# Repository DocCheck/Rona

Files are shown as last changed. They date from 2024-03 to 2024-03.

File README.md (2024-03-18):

# Rona - the Robotic Nurse Assistant

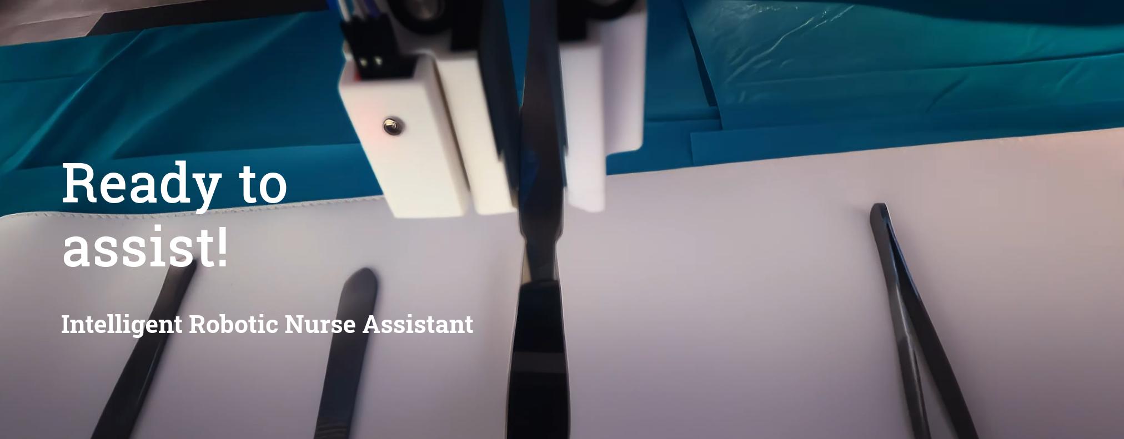
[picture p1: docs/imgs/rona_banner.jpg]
(https://more.doccheck.com/en/rona/)


# Meet Rona - your Open Source assistant for surgical procedures

Rona is an upgrade kit for robotic arms designed to address the problem with declining numbers of nurses in hospitals in
Germany, but also around the world. Rona's development is dedicated to create an affordable, easy to use, one-of-a-kind
software upgrade for surgery procedures and interventions where an additional hand is required, but a human support
might not be available.

The idea is to build an add-on that can be modular enough to be applicable to different robotic arms.
The system can be used with customizable machine learning models for instrument detection, angle estimation and wake-word detection.

For more information visit also: https://more.doccheck.com/en/rona/ 

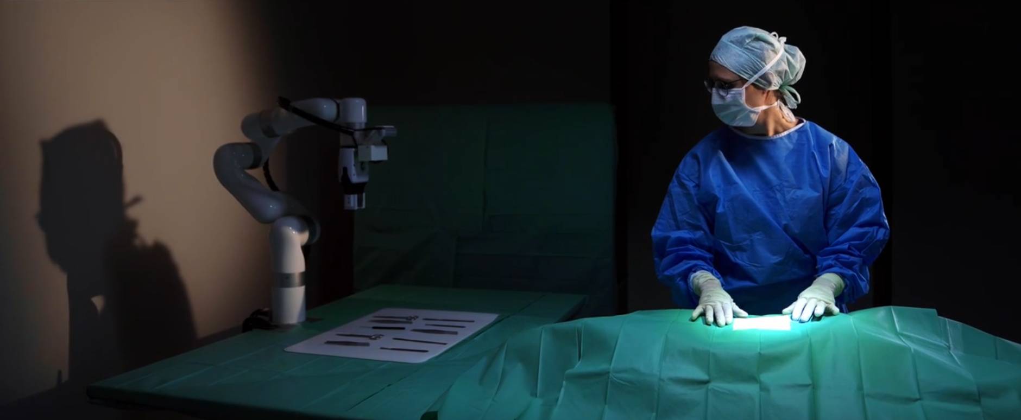
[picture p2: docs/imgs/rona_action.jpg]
Rona in Action (https://more.doccheck.com/en/rona/)


# Project Overview

## Requirements

### Hardware

Required hardware:

- a robotic arm. Currently only the [UFactory xArm5](https://www.ufactory.cc/xarm-collaborative-robot/) is supported
- a two-finger gripper e.g. [UFactory xArm Gripper](https://www.ufactory.cc/product-page/ufactory-xarm-gripper/) for the
  xArm5
- a camera holder for the robot e.g. [UFactory camera stand](https://www.ufactory.cc/product-page/ufactory-xarm-camera-stand/)
- a depth camera. Currently only the [Intel Realsense D435](https://www.ufactory.cc/xarm-collaborative-robot/) is  supported and tested in this setup
- a suitable microphone 
- a RaspberryPi Pico
- a [SW420 vibration sensor](https://www.az-delivery.de/en/products/sw420-vibration-schuttel-erschutterung-sensor-modul)
- 3D printable gripper tips, mounts and casings. CAD files can be found in the [3D models](docs/parts) folder
- cables and screws (more details in the assembly tutorial below)

For assembly and setup of the hardware parts check the [assembly tutorial](docs/assembly_tutorial.md) first.

### Software

Required software:

- [Linux machine with Ubuntu 22.04](https://ubuntu.com/download/desktop)
- [ROS2 Humble](https://docs.ros.org/en/humble/Installation.html)
- [Python 3.10+](https://www.python.org/downloads/)
- [Intel® RealSense™ SDK 2.0](https://github.com/IntelRealSense/librealsense/blob/master/doc/distribution_linux.md)
- [UFactory xArm-Python-SDK Version 1.13.0](https://github.com/xArm-Developer/xArm-Python-SDK) 
- various libraries python libraries explained in the [quickstart guide](docs/quickstart.md)

To install the software and the necessary libraries follow the [quickstart guide](docs/quickstart.md) \
For more detailed information on each ROS2 module check the [module documentation](docs/modules.md).

## Installation
- Get the necessary hardware listed in the [assembly guide](docs/assembly_tutorial.md) and follow it for the full assembly of the system.
- Follow the [quickstart guide](docs/quickstart.md) and install the necessary software, train or download all the necessary models for instrument detection, angle estimation and wake-word detection. 
- Do the [one-time configurations](docs/config.md) before you can continue with the usage of Rona

# How to use Rona
## Starting the system
Make sure you followed the [assembly guide](docs/assembly_tutorial.md), the [quickstart guide](docs/quickstart.md) and the [configuration](docs/config.md) before proceeding.
If everything is done successfully, you can start with the following commands in the rona_ws/ folder:

```bash
# Build and source the packages again just in case
$ make build-workspace

# Start system
$ make start-system
```

When Rona successfully boots up she will inform the user vocally that she is ready. 

## Wake word
In idle mode Rona will listen for her wake-word "Hey, Rona...". If she hears it she will open her gripper to signal that she starts listening for commands. 

          User: "Hey, Rona..."
          Rona: *opens gripper and starts listening to commands* 

The default listening time is 5 seconds. 
After this time she will close her gripper and go back to idle mode.

## Voice Commands
The system has 3 main commands for handling instruments: 
- *give/take* - Give an instrument from the tray to the surgeon
- *return* - Return an instrument from the surgeon to the tray
- *change* - First return an instrument, then take an instrument from the tray.

In addition to this there are 5 commands for system control:
- *cancel* - Cancel the current command
- *recalibration* - Recalibrates the transfer position
- *reset* - Reset the system
- *save* - saves the calibration
- *shut down* - shuts down the system and Rona will move into the shutdown position

## Dialogue Flow

Rona will indicate that she heard the wake word by opening her gripper. While the gripper is open, she is listening for commands. When the gripper is closed
you need to say the wake-word again and wake her up. The default listening time is 5 seconds.  

* ***give/take***: Rona will scan the table for an instrument and will pick it up and bring it to the transfer position.
    She will confirm your choice vocally if she heard you correctly.

          U: "Give me the blunt scissors" / "Take the narrow scalpel"
          R: "Blunt scissors chosen" / "Narrow scalpel chosen"

    If the command is incomplete, for example you don't know which scissors you want or are available, she will help you
    out by listing out all the possible instruments of that variety automatically. And you can immediately repeat your
    answer to her to lock in the choice.

          U: "Give me scissors"
          R: "Wrong input! You can choose between blunt and pointed scissors."
          U: "Blunt scissors"

    If she for any reason could not find the instrument after a couple of seconds, she will tell you and go back to sleep.

          U: "Give me the blunt scissors"
          R: "Could not find instrument"

    If you don't take the instrument after some time she will cancel the give command, return it back to its place and
    will move back to home position to scan and wait for your wake-word and command.

* ***return***: Rona will scan the instrument table for free slots and checks if any are missing (because you have taken
  them). If you call for return when you don't have an instrument, she will tell you that it is not possible and that
  all instruments are on the table. Otherwise, she will go to the transfer position and await for you to return your
  instrument.

        U: "Return"
        R: "Return has been chosen" / "Return is not possible, instruments are on the table"

  If you don't place the instrument in the gripper after some time she will cancel the return and move back to home
  position to scan and wait for your wake-word and command.

  The returning position is picked with the help of the empty slot detector. As mentioned in the previous chapter the
  detector should be setup depending on how many instruments you have, but generally there will always be at least one
  free slot if you have already taken an instrument and want to return or change. Typically, the empty slot is chosen at
  random if there is more than one available.

* ***change***: Rona will change one of your instruments with a new one of your choosing. This means she expects you to
  first return one instrument, and then she will give you the one you asked for immediately after that. This is basically
  like *return + give* in one sequence, so all the rules and conditions from their separate calls are the same for this
  command as well.

        U: "Change with narrow scalpel"
        R: "Changing with narrow scalpel" / "Could not find instrument"

  If you fail to return the instrument during the return window, you will not get your new instrument and will have to
  invoke a command anew.

These 3 commands are Rona's bread and butter and now is a good time to talk about the key point in all of them - that is
the transfer. To have a successful transfer in any of the commands, we need to check-off 3 security steps. These checks
start the moment Rona arrives at the transfer position.

1. ***hand detection***: Rona starts the camera and runs the hand detection. If she sees an arm she starts the second
   check which is the depth measurement. If the hand exits the frame before completing the first two checks, the
   scanning resets and starts again from the hand detection.

2. ***distance measurement***: Rona checks if the seen hand is close enough to the gripper for a transfer to occur. We
   wouldn't want to see a hand somewhere in frame and then Rona just assuming it is time to release the instrument and
   drop it on the patient. If the hand is in the right position near the gripper the third check starts.

3. ***shock sensor***: Rona starts checking for an impulse on her gripper tip - meaning you either put an instrument
   there, and she should close the gripper and take it - or you've grabbed the instrument with your hand, and she should
   release it. In both cases she delays for about a second before starting to move again, so that you can remove your
   hand from her.

If no impulse is detected in a given time, she starts the check again from the beginning, if the system's maximal
transfer time hasn't expired yet. There is a bit of getting used to passing the transfer safety checks, but there is
relatively big freedom of movement for the user. The main things are to approach the instrument from the side where the
camera is and tap the gripper tip that has the sensor in it. In the demo section we have provided some visual examples,
so check them out.

Next we want to briefly explain the system control commands.

* ***reset***: If Rona gets stuck because of a kinematic error she won't be able to move until getting her motors
  unblocked first. With the reset command we can unblock Rona and reset her to her home position.

        U: "Reset"
        R: "The system is resetting"

* ***shut down***: At the end of the use we can shut down Rona with this command. All her services will exit cleanly,
  she will move down to her shutdown position and will turn off. We still need to turn of the robot arm manually though.

        U: "Shut down"
        R: "The system im shutting down"

* ***recalibration***: If we want to change the transfer position while the system is online , for example during a
  surgery it needs to be moved. With this command the robot arm goes into manual moving mode, and we can grab the arm and
  adjust it in any position we desire. This is very helpful, because we can visually see where the new transfer point is
  going to be, and we have all the freedom to adjust it properly.

        U: "Recalibrate"
        R: "Recalibration started"

From here we have two choices, we can either ***save*** or ***cancel*** the recalibration with the respective commands.
If we try to give any other instructions instead, Rona will prompt us to save changes before we can continue. This means
we either have to save or cancel before we can get back to normal operations.

With this we are armed with all the knowledge needed to use Rona! Check out the next section for more visual examples
and the Roadmap section to see what we still plan to do in the future. Of course, feel free to leave any suggestions or
make any improvements of your own!

#  Customizable Machine Learning Models 
Rona uses several machine learning models for different tasks. To enable a wider range of potential use cases each model can be trained and customized to the user's specific needs following the guides in separate repositories. \
For experimentation we provide pretrained models on huggingface.

### Surgical Instrument Detection
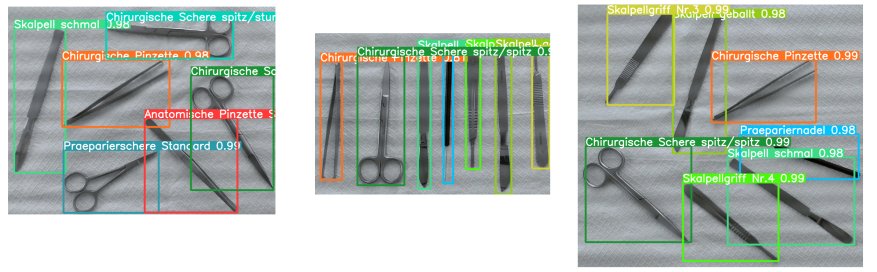
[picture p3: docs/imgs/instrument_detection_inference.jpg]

- YOLOv5 architecture custom trained on 12 different surgical instruments
- More details and a guide for customized training can be found in our separate [Surgical Instrument Detection repository](https://github.com/DocCheck/Surgical-Instrument-Detector/)
- Our trained model can be downloaded from [huggingface](https://huggingface.co/DocCheck/medical-instrument-detection).

### Instrument Angle Estimator
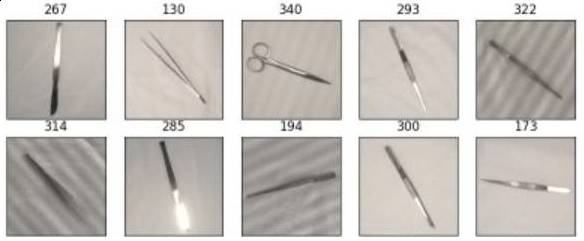
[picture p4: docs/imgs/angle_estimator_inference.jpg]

- Modified RotNet architecture custom trained to estimate the angles on 12 different surgical instruments
- More details and a guide for customized training can be found in our separate [Instrument Angle Estimator repository](https://github.com/DocCheck/Instrument-Orientation-Estimator/)
- Our trained models can be downloaded from [huggingface](https://huggingface.co/DocCheck/medical-instrument-orientation-estimation). 

### Wake-word detection 
- OpenWakeWord model trained on the activation phrase "Hey, Rona"
- More details and a guide for customized training can be found in the great [OpenWakeWord repository](https://github.com/dscripka/openWakeWord)
- Our trained model can be downloaded from [huggingface](https://huggingface.co/DocCheck/wakeword-hey-rona).

# How To Get Involved
Do you want to support the development? We are always looking for new contributors and feedback.
### Bugs and issues
If you found an issue or have a feature request, please open an issue on the [issue tracker](https://github.com/DocCheck/Rona/issues)

### Code contribution
If you want to contribute to the code by implementing new features or port the system to a different robotic arm, feel free to contribute to this project and the related repositories.

### Partnering up
If you want to partner up with us and continue the developing the project with us, please contact us at: https://more.doccheck.com/en/rona/

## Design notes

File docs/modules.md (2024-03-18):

# ROS2 modules
Rona is a ROS2 project and is developed on 'ROS2 humble'. The reason we chose to use ROS2 as a developer platform for the project is the modularity that it brings. Rona aims at being flexible and easy to customize for different scenarios - and the modules' structure allows just that. Speaking of the modules, the system is split into 5 main modules and 3 extra modules, some of which should be adjusted and (if needed) rewritten for the specific robotic arm that is being used.

List of Rona's modules:
1. [camera module](#camera-module-and-the-intel-realsense-d435)
2. [voice recognition module](#voice-recognition-module)
3. [speaker module](#speaker-module)
4. [sensor communication module](#sensor-module)
5. [main algorithm module](#main-algorithm-module)
6. [(manual control module)](#manual-control-module)
7. [(calibration module)](#calibration-module)
8. [(robot handler module)](#robot-handler-module)
9. [config](#rona-config)

Each module uses one or more open source libraries that take into consideration the other very important trait of the Rona system - the whole project runs completely offline without internet connection. This was the main goal from the very beginning, because being a medical assistant and crashing in the middle of an intervention do to bad internet connectivity would be very ... inconvenient. Thus, all the modules are designed with that in mind. In the next section we will discuss what each module does and which libraries are needed to be installed.

## Camera module and the Intel Realsense D435

Let us start with arguably the most important module of the system - the robot's vision. Rona's vision requires a depth camera with a good depth sensor and generally good resolution - **with a minimum requirements of 1280x720 capability for both frames** . For our research and development we have chosen the **Intel Realsense D435**. Of course there is a possibility to exchange that camera with another of the Realsense series or even another depth camera in general, depending on budget and needs. Our research was done with this camera, so we will base all further explanations based on usage of that model.

---

The camera module is divided internally into different submodules. The first one is the **object detection**. As an example we have trained a custom machine learning model for surgery instruments and have used the Yolo_v5 library for real-time instrument detection. The main model is based on the instruments used in a more simple surgery, namely - scalpels, scissors, tweezers, scalpel handles and needles. It actually contains not only an *instrument detection model*, but also an *orientation estimation model* that calculates tha angle at which the instrument is seen and also *empty space image processing* for the returning of the instruments to the table. We provide the trained models from the project and some samples to go with them for clarification in our *repositories* [1](https://github.com/DocCheck/Instrument-Orientation-Estimator/) [2](https://github.com/DocCheck/Surgical-Instrument-Detector/) and the models from our *huggingface* [1](https://huggingface.co/DocCheck/medical-instrument-orientation-estimation) [2](https://huggingface.co/DocCheck/medical-instrument-detection)

Regarding any parameters you can adjust for the detector, you can check the *general_config.py* in the *instrument_detector* folder. For example, adjusting the size of the grid to your needs, depending on the amount of instruments you are using. A good practice is to setup the robot's workspace range, which is defined by the frame of view of the camera, and use the *test_instrument_detection.py* test function you can find in the test folder to adjust the position of the instruments and play around with the grid size.

---

The next submodule is the **hand detection**. We use hand detection during the instrument transfer where we detect the hand and its distance to the gripper to try and minimize the errors during the transfers. We found Google's [*mediapipe*](https://developers.google.com/mediapipe/solutions/vision/hand_landmarker) library working great for our purpose so we use the hand landmark detection from Mediapipe. Unfortunately, during our development Mediapipe got a massive overhaul from Google and the newest version 0.10.* actually performed worse than the old 0.9.* version, because of the algorithm changes to their hand detection. Thus for the hand detection to be working properly with highest efficiency we recommend using the **mediapipe 0.9.3** version. The correct version for the library is linked in the requirements.txt file you should install with the help of the [quick start guide](quickstart.md)

---

The third submodule is reserved for an automated eye-in-hand calibration of the camera's position in case there is a decision to change the camera and/or change the position and angle of the camera holder. Currently it is only a placeholder, but could be expanded later. The actual camera coordinates are saved in the *config_rona.py* with the geometry when using the UFactory xArm5 and our designed 3D printed camera holder. 

If you followed everything until now, you should have everything set up correctly for the camera module. Time to move to the next one.

## Voice recognition module

The second most important module for the system is the voice recognition module. Because our goal was to develop a hands-free assistant, we had to resort to complete voice control over the system - making the experience as authentic as possible to working with an actual human nurse, where you would simply tell her what instrument you need without any physical inputs. 

Similar to the camera module, the voice recognition module has submodules. As with any good voice assistant Rona needed to have a wake-word which can trigger the voice recognition. We wouldn't want the medical team to casually talk about the instruments and Rona flying around with a scalpel when the team isn't ready for it, now do we. For this reason we decided to use the open-source [openWakeword](https://github.com/dscripka/openWakeWord) library which is working completely offline and functions super reliably. It provides some pre-trained models, but most importantly it allows for training new custom wake-words. That is why we trained our own wake word "hey Rona" with which we wake up the system every time before we want to give a command. You can download the wake-word model from our [huggingface](https://huggingface.co/DocCheck/wakeword-hey-rona) and put it in the */rona_pkg/rona_pkg/voice_recognition/model_wakeword/* folder, if you haven't done it already. 

Also if you wish to train your own custom wake-word, check out the documentation here: [model training](https://github.com/dscripka/openWakeWord/blob/main/notebooks/training_models.ipynb)

---

After waking up the system we start the next submodule which is now the full voice recognition. Because we are opting for a completely offline system, we had limited possibilities when it came to voice recognition. Luckily, [whisper](https://github.com/openai/whisper) from openAI is an excellent free and offline voice recognition library that provides a large variety of models in different languages and sizes. In our r&d we found out that the "tiny" size model is working sufficiently accurate and fast enough for the system to feel smooth and realistic - without too much processing delay. The model you would use needs to be downloaded first. The download of the model happens automatically the first time when you use that specific model and then you can use it anytime and offline. You can change the model if you want to by changing the related variable in *config_rona.py* script. 

Whisper takes the spoken words and transcribes them into strings which then get further processed by an intent recognizer - to see if any of the spoken words trigger a command. This also doubles as a filter in case whisper sometimes mishears your command or the instrument you want with another word. This could happen rarely and it can be influenced by many things like noise or bad microphone. As good as whisper is, we recommend getting a high-end microphone or a headset to ensure as few as possible errors with the command inputs. Rona works with predefined list of commands which could be expanded if needed. What they are and how to use them is explained in the main [README.md](../README.md).

For all sound inputs recordings we use the python [speech_recognition](https://pypi.org/project/SpeechRecognition/) library. Pyaudio and torch are also needed. All the necessary libraries for the voice recognition are included in the requirements.txt file you should install with the help of the [quick start guide](quickstart.md)

## Speaker module

We wanted Rona to feel alive so we gave her a voice to reply to you. Audible feedback is always appreciated, especially in situations when you aren't able to focus on some blinking lights or other visual cues - like during a surgery. We gave Rona some predefined lines, because we want to keep the system offline and the offline TTS sound very underwhelming. So we used the Google TTS to record some lines for her in a clear female voice and packed them inside the system. Of course this leaves the opportunity to expand her repertoire and add more custom lines if needed. We also use the speaker module as a guide while conversing with her. When you try and give a command, Rona can guide you towards the complete command while asking you further questions until she understands you or decides to cancel and start over. To be able to use the module you just need to have the [playsound](https://pypi.org/project/playsound/) library installed - this is again included in the requirements.txt file you should install with the help of the [quick start guide](quickstart.md)

## Sensor module

On top of the camera we wanted another safety level during the transfer of the instruments. We tried many different combinations and variations of sensors and ultimately stopped on an impulse sensor module controlled by a RaspberryPi Pico. The size of the module and the controller fit quite nicely in custom made 3D printed parts that we have also provided for free [here](parts/). With an assembly guide you can find [here](assembly_tutorial.md).The [sensor](https://www.az-delivery.de/en/products/sw420-vibration-schuttel-erschutterung-sensor-modul) is a sw 420 vibration sensor and its idea is to only open or close the gripper when there is a "haptic" feedback, meaning someone or something touched the gripper tip. This way we can ensure that instruments won't get dropped on the floor or the gripper won't close without an instrument in it. 

We use the [python serial](https://pypi.org/project/pyserial/) library to exchange information between the RBP and the workstation, thus they need to be connected with an USB cable during use. The simple yet effective sensor communication module ensures that the signal from the sensor can get used in the ROS2 environment as a trigger for the next actions. We need the python serial library for that, which can be installed via:

Sometimes you might need to unblock the serial port while connecting to the controller. You can do this with the command **sudo chmod a+rw /dev/ttyACM0**

Additionally, you need to have the proper code running on the RaspberryPi. Check out how to configure the RaspberryPi in the [one-time configuration tutorial](config.md) 

## Main algorithm module

This is technically Rona's brain. This is the main module and the main node for the ROS2 system. Here all the service calls are done based on the commands and the communication between all the nodes happens. A more thorough explanation of the system's action sequences is given in the main [README.md](../README.md). 

## Manual control module

In case you want more controlled testing or you don't want to use voice commands for some reason, we have added an additional module which you can substitute the voice control module with. This way you can publish on the manual control command topic a list with information about the command (check the command dictionary in the module) and the system will execute this command as if you have given it a vocal command. This module is intended for debugging and more controlled testing of some edge cases, but we decided to leave it so that it can be used or further developed if needed. To activate it you need to comment and uncomment the lines in the *main_rona.py* where the voice recognition service is initialized in the constructor - to essentially change the service that is being used. Of course the launch file needs to be adjusted properly as well.

## Calibration module

This is the module where the calibration information is saved. Mainly we need the eye-in-hand camera position based in the robot's base coordinate system and also the coordinates of the point of transfer. Currently there is no automated initial camera calibration for the eye-in-hand calibration, but could be added in future updates or can be done by yourselves following any eye-in-hand calibration tutorial with a fiducial or QR code. The drop-off coordinate point can be manually changed as you please and also there is a command for dynamic recalibration of that point while the robot is running. This recalibration will **not** overwrite the values in the script permanently. It is only for the actual use cycle of the robot - after you shut the system down and start anew the old transfer point.

## Robot handler module

Finally, we have written a robot handler for quicker and easier access to the robot functions and movements. Of course this module is specific to the robot hand being used. For our development we used the UFactory xarm5 and their [Python-SDK](https://github.com/xArm-Developer/xArm-Python-SDK) respectively.
To clone and prepare the repository for use with Rona follow the [quick start guide](quickstart.md)

In the "config_rona.py" you will find some kinematic parameters that have been found to be the most optimal, but you can change them around if you please. In the handler you will find a small dictionary with width values of the instruments, because the gripper of the robot doesn't have any force or torque sensors. So to insure proper holding of each instrument we need to adjust for the instruments' width. The rest of the functions are a combination of simple movements summarized into one command. All of the movements are in joint coordinate system, so that the sharper faster movements are possible. For further information on the xArm commands, you can check out the examples in the SDK provided by UFactory.

## Rona config

Lastly, a quick mention of the config file. In the config file you can find all the parameters you could change around if needed and also all of the path files for the different modules. The values there have been tuned for the most optimal experience after our extensive testing, but you can change them around if needed.

---

This concludes the fast overview of the system and its modules. In the next section we will explain the usage, logic and configuration of the system with examples, pictures, videos and charts.

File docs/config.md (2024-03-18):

Here you can find a quick guide to the "one-time" configuration you need to perform in the beginning, before you can use Rona

## RaspberryPi

To setup the RBP we recommend using [Thonny](https://thonny.org/), because the code is written in Pi Python. Download and install Thonny and then you can use it to run the code on the RBP. You can find the code in the */rona_pkg/rona_pkg/sensoric/* folder. You need to upload the main.py file to the controller. We have also provided the code as a text file just in case. To upload the file to the RBP you first connect it to the workstation via the USB cable. Open a terminal and unblock the port using **sudo chmod a+rw /dev/ttyACM0**. In the same terminal directly run *thonny*. If the interpreter doesn't get configured automatically,go to the *Run* menu on the toolbar and choose *configure interpreter*. From the menu there select the RBP board. Then use *open* and choose *This computer*. Navigate to the /sensoric folder and open the *main.py*. Afterwards *"save as..."* to the controller preserving the same name *main.py* and run it from thonny with the run button. Now close thonny and the terminal. 

If something went wrong, you can check a very useful tutorial [here](https://www.youtube.com/watch?v=L03jT5slWnw) and then try again.

## Robot arm

To be able to connect to the xArm we need to set the LAN IP Address of the Ethernet port of our workstation - where we would connect the robot - to static, so that the robot can be found. We use the following configurations:

    Address 192.168.1.12
    Netmask 255.255.255.0
    Gateway 192.168.1.1

Before use and testing, release the red safety button on the controller to enable the motors of the robot and be vigilant that the robot can move now.

## Testing

It is advised to test all the connections before starting the whole system. We have provided a few test functions you can use to check:

- Realsense camera connection : **test_camera_intel.py**
- RBP connection: **test_controller_connection.py**
- Robot connection: **test_robot_connection.py**

You can also use the Makefile commands directly:

make test-camera
make test-controller
make test-robot

When using the RBP test, first unlock the port if needed **sudo chmod a+rw /dev/ttyACM0** and after starting the test - shake the sensor to see the feedback.

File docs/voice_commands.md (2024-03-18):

# Voice Commands

We are using a three-step system to allow a fast and reliable voice recognition. 
- Phase 1: Wake word detection with [OpenWakeWord](https://github.com/dscripka/openWakeWord) model trained on the phrase "Hey Rona..."
- Phase 2: Speech to Text with [Whisper by OpenAI](https://openai.com/research/whisper)
- Phase 3: Text-based intent recognition

This method enables us to achieve fast processing when Rona is in idle mode while ensuring high precision while listening to the user's commands. 
The intent recognition allows to filter for common errors and customizable commands.

## Wake word detection
In idle mode Rona will listen for her wake-word "Hey, Rona...". If she hears it she will open her gripper to signal that she starts listening for commands. 

          User: "Hey, Rona..."
          Rona: *opens gripper and starts listening to commands* 

The default listening time is 5 seconds. 
After this time she will close her gripper and go back to idle mode.

### Available Voice Commands
The system has 3 main commands for handling instruments: 
- *give/take* - Give an instrument from the tray to the surgeon
- *return* - Return an instrument from the surgeon to the tray
- *change* - First return an instrument, then take an instrument from the tray.

In addition to this there are 5 commands for system control:
- *recalibration* - recalibrates the transfer position
- *reset* - reset the system
- *save* - saves the recalibration
- *cancel* - cancel the recalibration
- *shut down* - shuts down the system and Rona will move into the shutdown position

### Command Dialogue Flow

Rona will indicate that she heard the wake word by opening her gripper. While the gripper is open, she is listening for commands. 
* ***give/take***: Rona will scan the table for an instrument and will pick it up and bring it to the  transfer position. She will confirm your choice vocally if she heard you correctly.

        U: "Give me the blunt scissors" / "Take the narrow scalpel"
        R: "Blunt scissors chosen" / "Narrow scalpel chosen"

    If the command is incomplete, for example you don't know which scissors you want or are available, she will help you out by listing out all the possible instruments of that variety automatically. And you can immediately repeat your answer to her to lock in the choice.

        U: "Give me scissors"
        R: "Wrong input! You can choose between blunt and pointed scissors."
        U: "Blunt scissors"

    If she for any reason could not find the instrument after a couple of seconds, she will tell you and go back to sleep - awaiting your wake-word.

        U: "Give me the blunt scissors"
        R: "Could not find instrument"

    If you don't take the instrument after some time she will cancel the give command, return the instrument back to its place and will move back to home position to scan and wait for your wake-word and command. 

* ***return***: Rona will scan the instrument table for free slots and checks if any are missing (because they have been taken). If you call for return when you don't have an instrument, she will tell you that it is not possible and that all instruments are on the table. Otherwise she will go to the transfer position and await for you to return your instrument.

        U: "Return"
        R: "Return has been chosen" / "Return is not possible, all instruments are on the table"

    If you don't place the instrument in the gripper after some time she will cancel the return and move back to home position to scan and wait for your wake-word and command. 

    The returning position is picked with the help of the empty slot detector. As mentioned in the previous chapter he detector should be setup depending on how many instruments you have, but generally there will always be at least one free slot if you have already taken an instrument and want to return or change. Typically, the empty slot is chosen at random if there is more than one available.

* ***change***: Rona will change one of your instruments with a new one of your choosing. This means she expects you to first return one instrument and then she will give you the one you asked for immediately after that. This is basically like *return + give* in one sequence, so all the rules and conditions from their separate calls are the same for this command as well.

        U: "Change with narrow scalpel"
        R: "Changing with narrow scalpel" / "Could not find instrument"

    If you fail to return the instrument during the return window, you will not get your new instrument and will have to invoke a command anew.

These 3 commands are Rona's bread and butter and now is a good time to talk about the key point in all of them - that is the transfer. To have a successful transfer in any of the commands, we need to check-off 3 security steps. These checks start the moment Rona arrives at the transfer position.

   1. ***hand detection***: Rona starts the camera and runs the hand detection. If she sees an arm she starts the second check which is the depth measurement. If the hand exits the frame before completing the first two checks, the scanning resets and starts again from the hand detection.

   2. ***distance measurement***: Rona checks if the seen hand is close enough to the gripper for a transfer to occur. We wouldn't want to see a hand somewhere in frame and then Rona just assuming it is time to release the instrument and drop it on the patient. If the hand is in the right position near the gripper the third check starts.

   3. ***shock sensor***: Rona starts checking for an impulse on her gripper tip - meaning you either put an instrument there and she should close the gripper and take it - or you've grabbed the instrument with your hand, and she should release it. In both cases she delays for about a second before starting to move again, so that you can remove your hand from her. 
   
If no impulse is detected in a given time, she starts the check again from the beginning, if the system's maximal transfer time hasn't expired yet. There is a bit of getting used to passing the transfer safety checks, but there is relatively big freedom of movement for the user. The main things are to approach the instrument from the side where the camera is and tap the gripper tip that has the sensor in it. In the demo section we have provided some visual examples, so check them out.

Next we want to briefly explain the extra commands.

* ***reset***: If Rona get's stuck because of a kinematic error she won't be able to move until getting her motors unblocked first. With the reset command we can unblock Rona and reset her to her home position.

        U: "Reset"
        R: "The system is resetting"

* ***shut down***: At the end of the use we can shut down Rona with this command. All her services will exit cleanly, she will move down to her shutdown position and will turn off. We still need to turn of the robot arm manually though.

        U: "Shut down"
        R: "The system im shutting down"

* ***recalibration***: If we want to change the transfer position while the system is online , for example during a surgery it needs to be moved. With this command the robot arm goes into manual moving mode and we can grab the arm and adjust it in any position we desire. This is very helpful, because we can visually see where the new transfer point is going to be and we have all the freedom to adjust it properly.

        U: "Recalibrate"
        R: "Recalibration started"

From here we have two choices, we can either ***save*** or ***cancel*** the recalibration with the respective commands. If we try to give any other instructions instead, Rona will prompt us to save or cancel changes before we can continue. This means we either have to save or cancel before we can get back to normal operations.

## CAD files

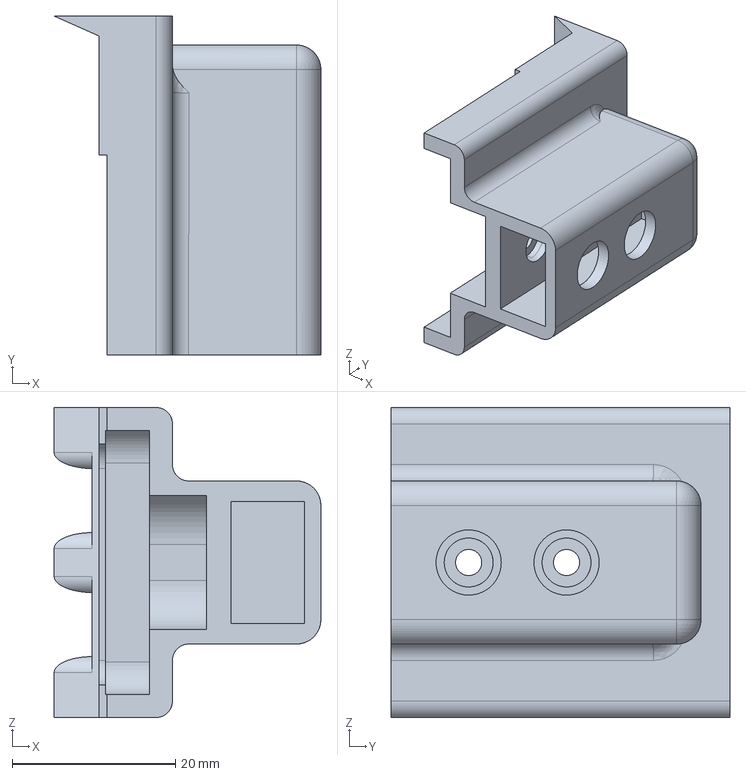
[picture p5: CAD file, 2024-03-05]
docs/parts/RonaTipCapLeft.step
32.7 x 41.6 x 38.0 mm

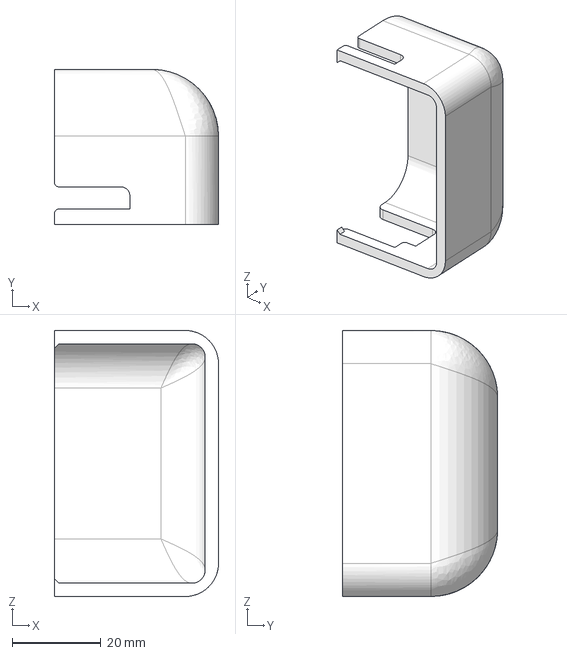
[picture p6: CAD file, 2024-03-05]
docs/parts/ControllerCover.step
37.0 x 35.0 x 60.0 mm

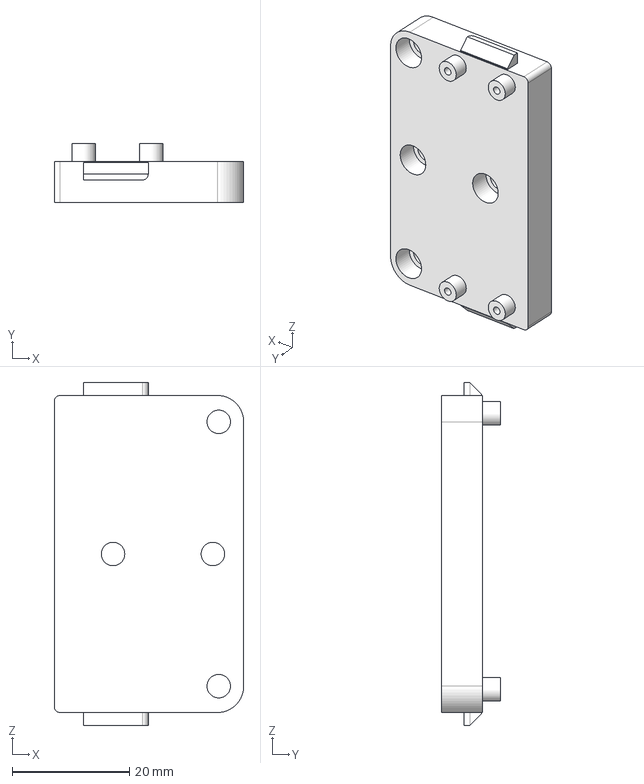
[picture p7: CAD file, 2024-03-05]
docs/parts/ControllerBed.step
32.2 x 10.0 x 58.4 mm

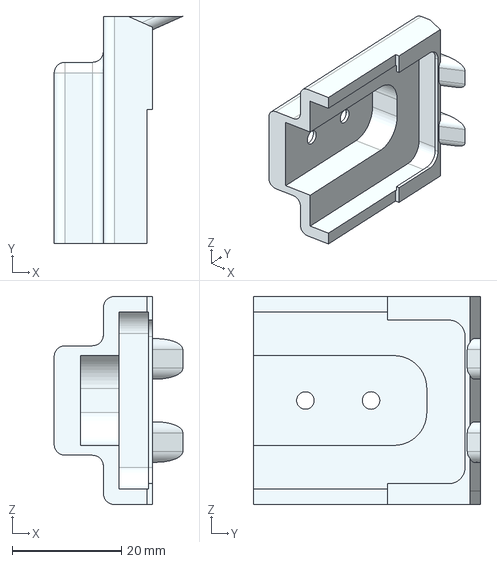
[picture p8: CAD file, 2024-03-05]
docs/parts/RonaTipCapRight.step
23.5 x 41.5 x 38.0 mm

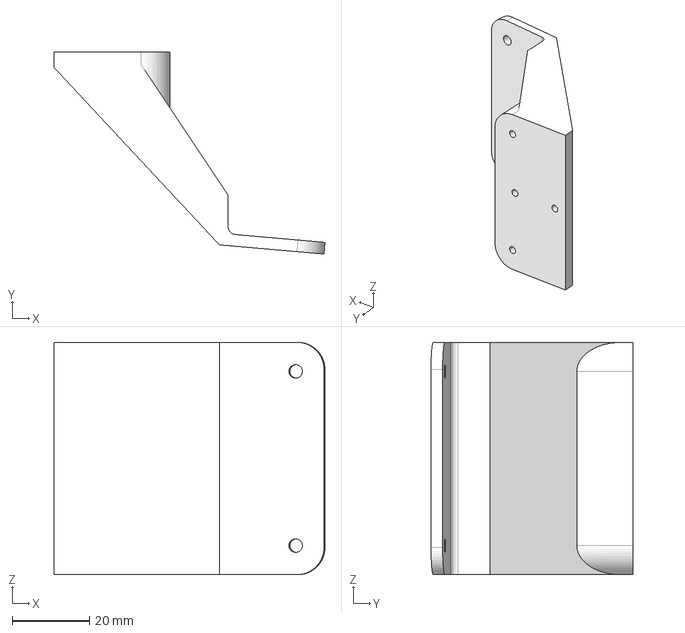
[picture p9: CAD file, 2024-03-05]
docs/parts/CameraExtension.step
70.0 x 52.2 x 60.0 mm

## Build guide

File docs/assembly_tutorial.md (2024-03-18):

This is an assembly tutorial for Rona's hardware.

**List of parts**:

- [UFactory xArm 5 robot arm](https://www.ufactory.cc/xarm-collaborative-robot/)
- [UFactory Gripper](https://www.ufactory.cc/product-page/ufactory-xarm-gripper/)
- [UFactory camera stand](https://www.ufactory.cc/product-page/ufactory-xarm-camera-stand/)
- [Intel RealSense D435 camera](https://www.intelrealsense.com/depth-camera-d435/)
- [Raspberry Pi Pico](https://www.az-delivery.de/en/products/raspberry-pi-pico)
- [sw420 vibration sensor module](https://www.az-delivery.de/en/products/sw420-vibration-schuttel-erschutterung-sensor-modul)
---
- Ethernet cable, 3m+ for the robot connection
- USB C 3.0+, 3m+ for the camera (preferably with a 90 degrees angle to the right)
- Micro USB, 3m+ for the controller (preferably with a 90 degrees angle to the right)
- 3 female-to-female jumper wire cables for the sensor
---
- 4x M3x10 self tapping screws for the controller bed / camera extension
- 1x M3x16 screw for the sensor and gripper tip cap
- 2x M3x10 screws for the simple gripper tip cap
- 4x M1.5x4/M1.5x5 self tapping screws for the controller
---
- Controller bed (3d printed)
- Controller cover (3d printed)
- Camera extension (3d printed)
- Gripper tip cap (simple) (3d printed)
- Gripper tip cap (sensor) (3d printed)

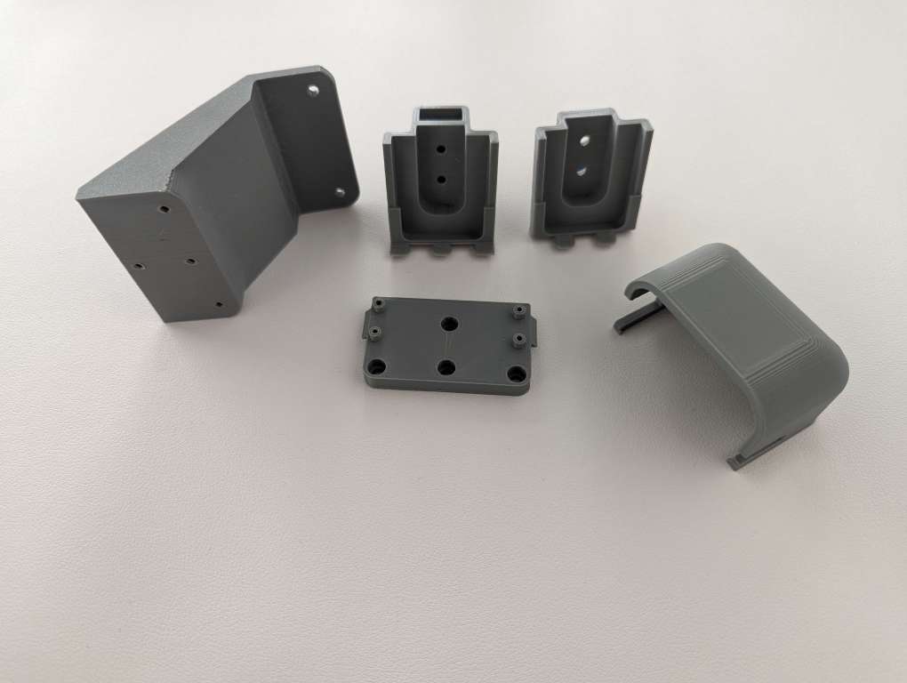
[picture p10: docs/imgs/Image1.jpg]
    

**Assembly**:

First of all mount the robot on a flat surface with enough space around it. Install the UFactory camera stand and the UFactory gripper next. Connect the power-control cable of the gripper to the robot flange. Take the simple gripper tip cap and install it over the original tips. To do so - unscrew the original gripper tips from the gripper and place them inside the caps. After that screw it back on by sliding it onto the gripper and using the 2x M3x10 screws tightening accordingly.

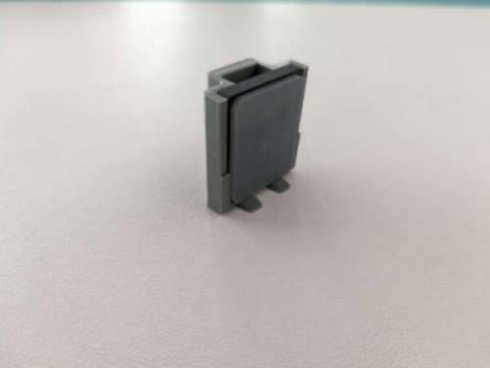
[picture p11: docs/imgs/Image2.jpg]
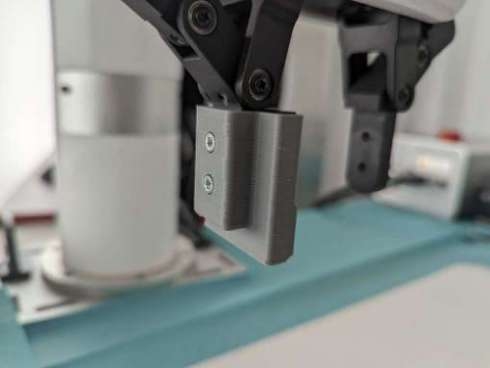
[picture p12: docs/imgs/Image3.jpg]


Take the sensor gripper tip cap next and put the sensor inside. Connect the jumper cables to the sensor pins before mounting the cap makes it easier to reach. The way we mount it is we screw everything together - cap, sensor and gripper with the 1x M3x16 screw. The screw goes through the upper hole (*red arrow*) of the cap and through the hole of the sensor and screws both cap and sensor tightly to the gripper. Through the bottom hole you can adjust the sensitivity of the sensor via the potentiometer without having to disassemble the gripper tip cap.

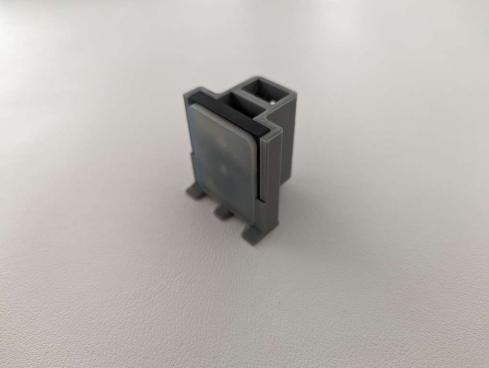
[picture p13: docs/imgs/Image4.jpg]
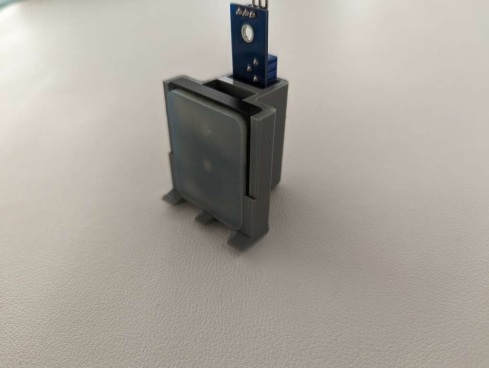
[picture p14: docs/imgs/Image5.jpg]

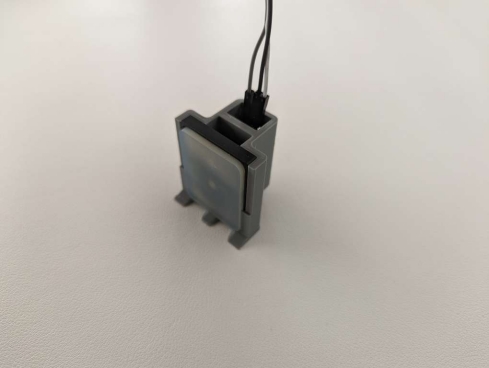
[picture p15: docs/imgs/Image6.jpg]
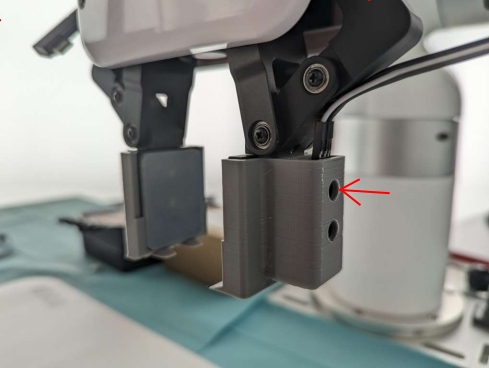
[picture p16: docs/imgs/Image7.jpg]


Next thing is positioning the camera extension on top of the UFactory camera stand and from the under side position the controller bed. Through the 4 holes on the bed screw it to the camera extension through the UFactory camera stand with the 4x M3x10 self tapping screws. 

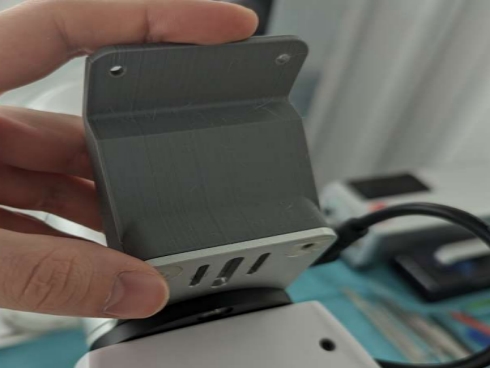
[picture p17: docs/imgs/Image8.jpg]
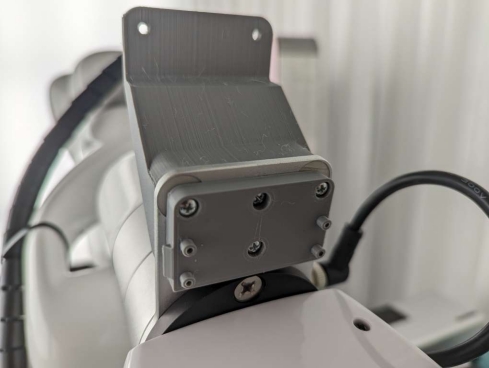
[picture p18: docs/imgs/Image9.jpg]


Next thing is to prepare the Raspberry Pi Pico. Typically the Pico comes unsoldered, which is good in our case. We need to solder the pins pointing upwards, so that it can be correctly mounted on the bed. After soldering, screw the Raspberry Pi to the controller bed via two to four of the M1.5x4 self tapping screws (or similar). Make sure to position the controller in the correct orientation, with the USB port pointing left, when you are looking at the robot from the front. After that plug in the jumper wire cables coming out of the sensor onto the correct pins of the controller, as shown in the diagram bellow. Finally, plug in the USB cable in the Pico to power it up.

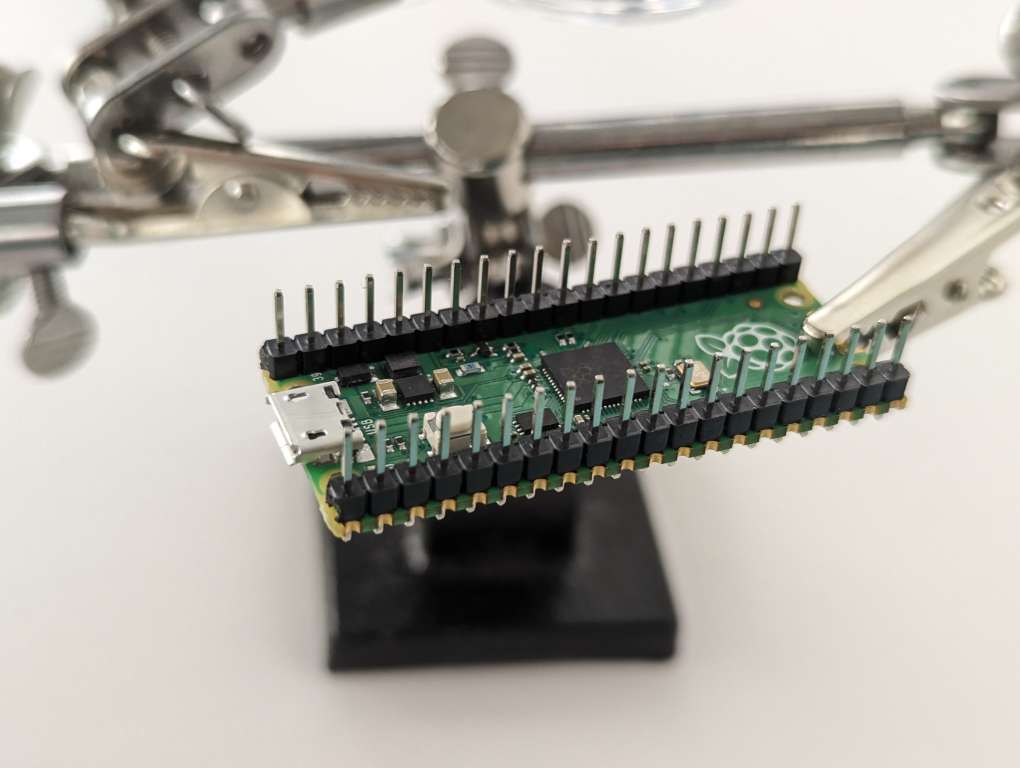
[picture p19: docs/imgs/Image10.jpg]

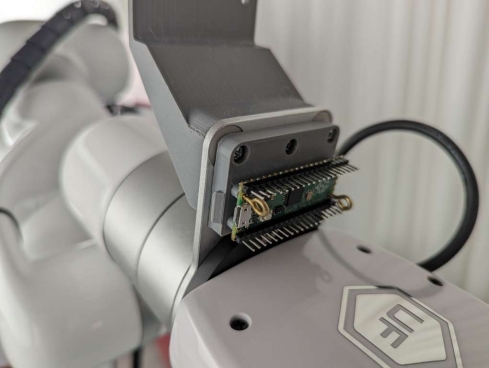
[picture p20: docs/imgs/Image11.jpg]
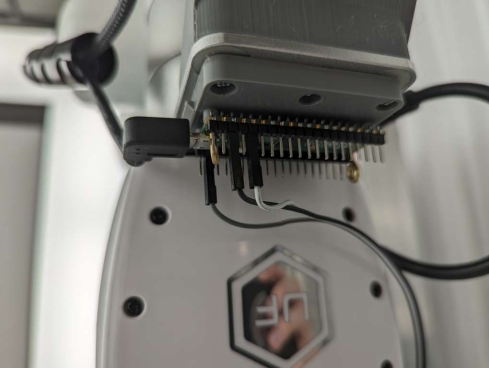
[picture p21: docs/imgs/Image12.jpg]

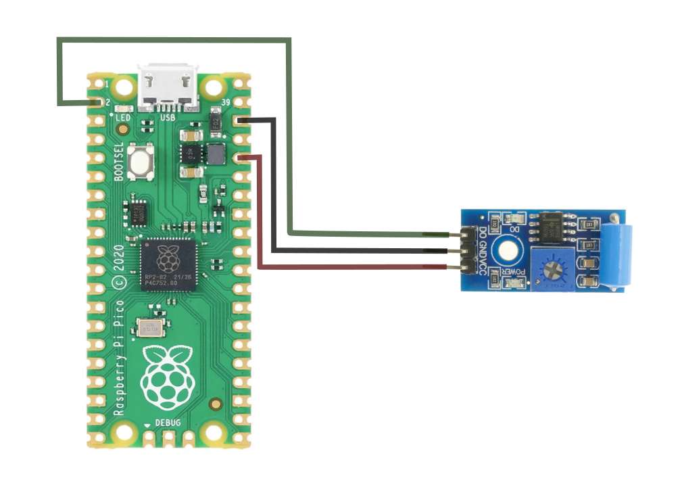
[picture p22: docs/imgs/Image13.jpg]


Now, carefully slide on the controller cover onto the controller bed. Bend the jumper cables a bit with your fingers so that they get inside the cover and don't bend any controller pins from the pushing. If everything is printed and assembled correctly, the cover should easily snap into place.

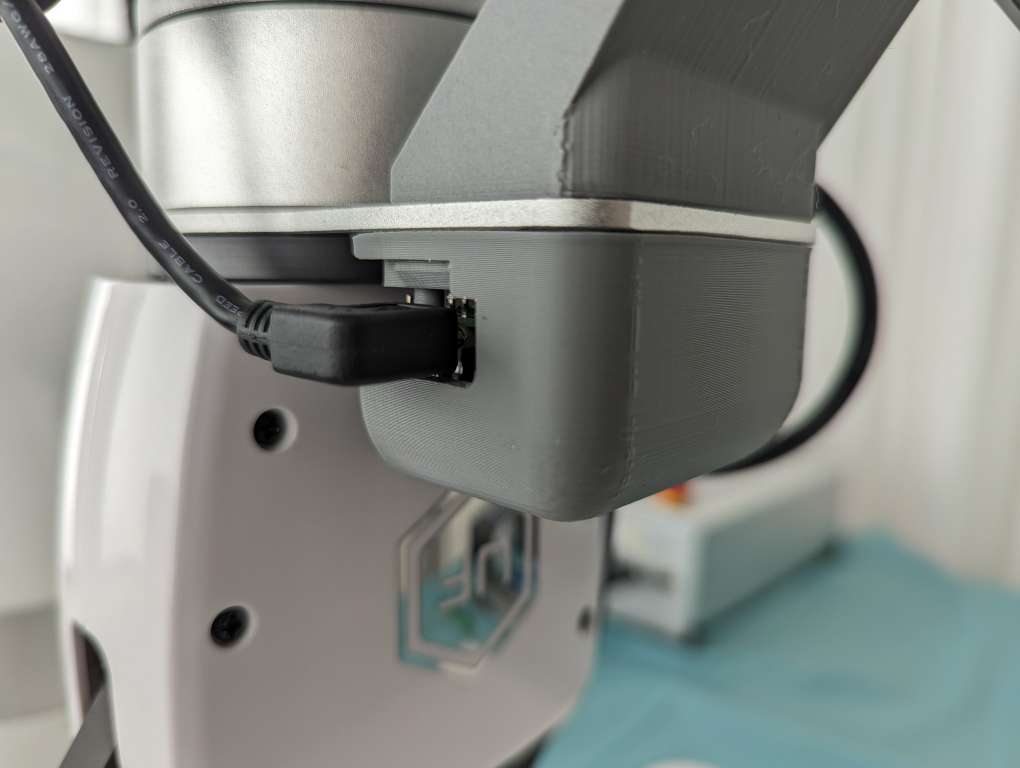
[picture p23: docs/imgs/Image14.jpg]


Lastly, screw the Intel camera to the camera extension and connect the USB C cable. 

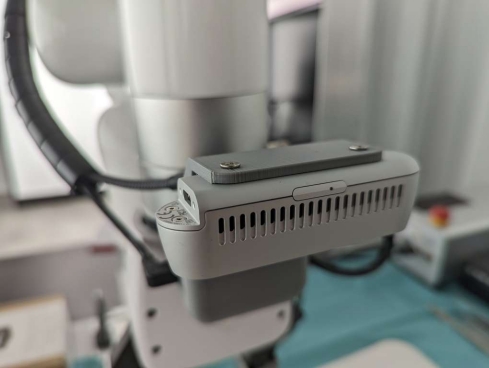
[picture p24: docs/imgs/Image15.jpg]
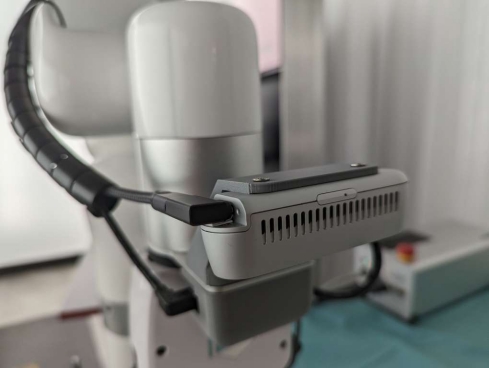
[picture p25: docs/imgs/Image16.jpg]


Finally, connect the cables of the UFactory controller to the robot arm and the Ethernet cable between the controller and your computer. Plug in the power cable for the robot controller. In the end the complete system should look something like this:

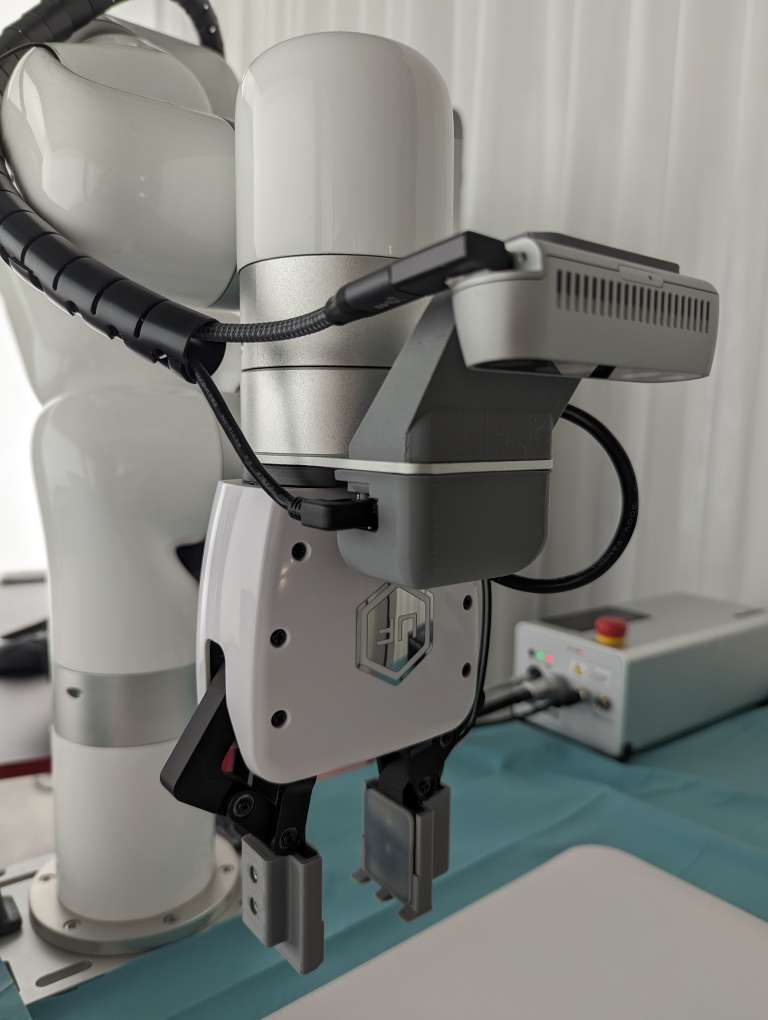
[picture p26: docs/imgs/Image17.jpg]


This concludes the system assembly. You should now move on to installing all the software via the README.md or if already done testing with the help of the test functions provided.

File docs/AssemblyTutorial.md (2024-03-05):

This is an assembly tutorial for Rona's hardware.

**List of parts**:

- [UFactory xArm 5 robot arm](https://www.ufactory.cc/xarm-collaborative-robot/)
- [UFactory Gripper](https://www.ufactory.cc/product-page/ufactory-xarm-gripper/)
- [UFactory camera stand](https://www.ufactory.cc/product-page/ufactory-xarm-camera-stand/)
- [Intel RealSense D435 camera](https://www.intelrealsense.com/depth-camera-d435/)
- [Raspberry Pi Pico](https://www.az-delivery.de/en/products/raspberry-pi-pico)
- [sw420 vibration sensor module](https://www.az-delivery.de/en/products/sw420-vibration-schuttel-erschutterung-sensor-modul)
---
- Ethernet cable, 3m+ for the robot connection
- USB C 3.0+, 3m+ for the camera (preferably with a 90 degrees angle to the right)
- Micro USB, 3m+ for the controller (preferably with a 90 degrees angle to the right)
- 3 female-to-female jumper wire cables for the sensor
---
- 4x M3x10 self tapping screws for the controller bed / camera extension
- 1x M3x16 screw for the sensor and gripper tip cap
- 2x M3x10 screws for the simple gripper tip cap
- 4x M1.5x4/M1.5x5 self tapping screws for the controller
---
- Controller bed (3d printed)
- Controller cover (3d printed)
- Camera extension (3d printed)
- Gripper tip cap (simple) (3d printed)
- Gripper tip cap (sensor) (3d printed)

    

**Assembly**:

First of all mount the robot on a flat surface with enough space around it. Install the UFactory camera stand and the UFactory gripper next. Connect the power-control cable of the gripper to the robot flange. Take the simple gripper tip cap and install it over the original tips. To do so - unscrew the original gripper tips from the gripper and place them inside the caps. After that screw it back on by sliding it onto the gripper and using the 2x M3x10 screws tightening accordingly.



Take the sensor gripper tip cap next and put the sensor inside. Connect the jumper cables to sensor pins before mounting the cap makes it easier to reach. The way we mount it is we screw everything together - cap, sensor and gripper with the 1x M3x16 screw. The screw goes through the upper hole (*red arrow*) of the cap and through the hole of the sensor and screws both cap and sensor tightly to the gripper. Through the bottom hole you can adjust the sensitivity of the sensor without having to disassemble the gripper tip cap.




Next thing is positioning the camera extension on top of the UFactory camera stand and from the under side position the controller bed. Through the 4 holes on the bed screw it to the camera extension through the UFactory camera stand with the 4x M3x10 self tapping screws. 



Next thing is to prepare the Raspberry Pi Pico. Typically the Pico comes unsoldered, which is good in our case. We need to solder the pins pointing upwards, so that it can be correctly mounted on the bed. After soldering, screw the Raspberry Pi to the controller bed via two to four of the M1.5x4 self tapping screws (or similar). Make sure to position the controller in the correct orientation, with the USB port pointing left, when you are looking at it. After that plug in the jumper wire cables coming out of the sensor onto the correct pins, as shown in the diagram bellow. Finally, plug in the USB cable in the Pico to power it up.





Now, carefully slide on the controller cover onto the controller bed. Bend the cables a bit with your fingers so that they get inside the cover and don't bend controller pins from the pushing. If everything is printed and assembled correctly, the cover should easily snap into place.



Lastly, screw the Intel camera to the camera extension and connect the USB C cable. 



Finally, connect the cables of the UFactory controller to the robot arm and the Ethernet cable between the controller and your computer. Plug in the power cable for the robot controller. In the end the complete system should look something like this:



This concludes the system assembly and you should be able to move on to testing with the help of the test functions provided and/or installing all the software via the README.md.
